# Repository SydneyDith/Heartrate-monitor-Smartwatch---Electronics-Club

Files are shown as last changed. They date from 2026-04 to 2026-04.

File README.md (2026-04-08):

# Heart rate Monitor Smartwatch - Electronics Club
Led the development of a heart rate monitor smartwatch based on the ATmega328P microcontroller with a group of 4. Utilized several sensors to send/receive data via I2C communication protocol using C based Arduino IDE. Designed custom PCB while analyzing several datasheets to reduce device size and create a more ergonomic user experience. 

This project was separated into two teams. Team 1 specialized in hardware development and was responsible for component selection, power distribution, datasheet analysis and PCB design. Team 2 interfaced with the microcontroller and sensors in the Arduino IDE by utilizing libraries like PulseSensor Playground, U8g2, and RTClib. While I primarily led Team 1, I also served as the mediator for cross-team communication to ensure hardware and software supported each other.

## Smartwatch Project Objectives

| Feature | Description | Goal |
| :--- | :--- | :--- |
| **Heart Rate Monitor** | Integrate Pulse Sensor | Provides heart rate measurements. |
| **OLED Display** | 1.3" SH1106 OLED Display | Clear visual output for biometric data and time. |
| **Timekeeping** | RTC (Real-Time Clock) | Maintain precise time and date. |
| **Power System** | Rechargeable LiPo | Provides rechargeable power. |

Throughout every iteration of this project we may have moved forward with different components that better fit our needs, however, the 4 underlying features above were included in every version of this project. 

## Proof of Concept: ***May 2025***

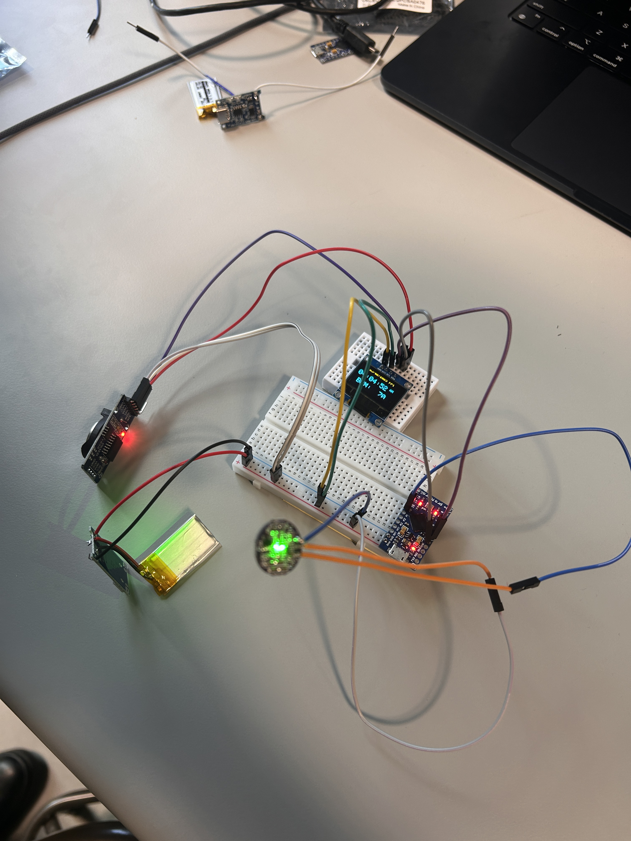
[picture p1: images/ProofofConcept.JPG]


The image above shows the first prototype of our Smartwatch. This version was based off of Arduino's smallest dev board the Pro Mini which houses the ATmega328P as its microcontroller (we would later use on the final versions of our project). To provide the functionalities we desired, we ordered several Arduino compatible modules that we could power and hook up to specific digital pins on the Pro Mini. In the table below is the comprehensive parts list we used for our first prototype:

| Feature | Part Name | Image |
| :--- | :--- | :--- |
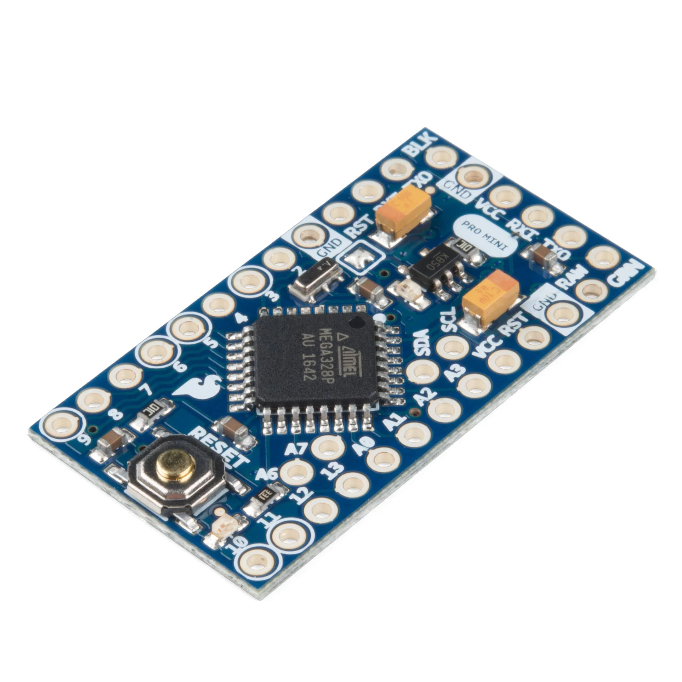
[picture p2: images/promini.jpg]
| **Microcontroller** | Arduino Pro Mini |  |
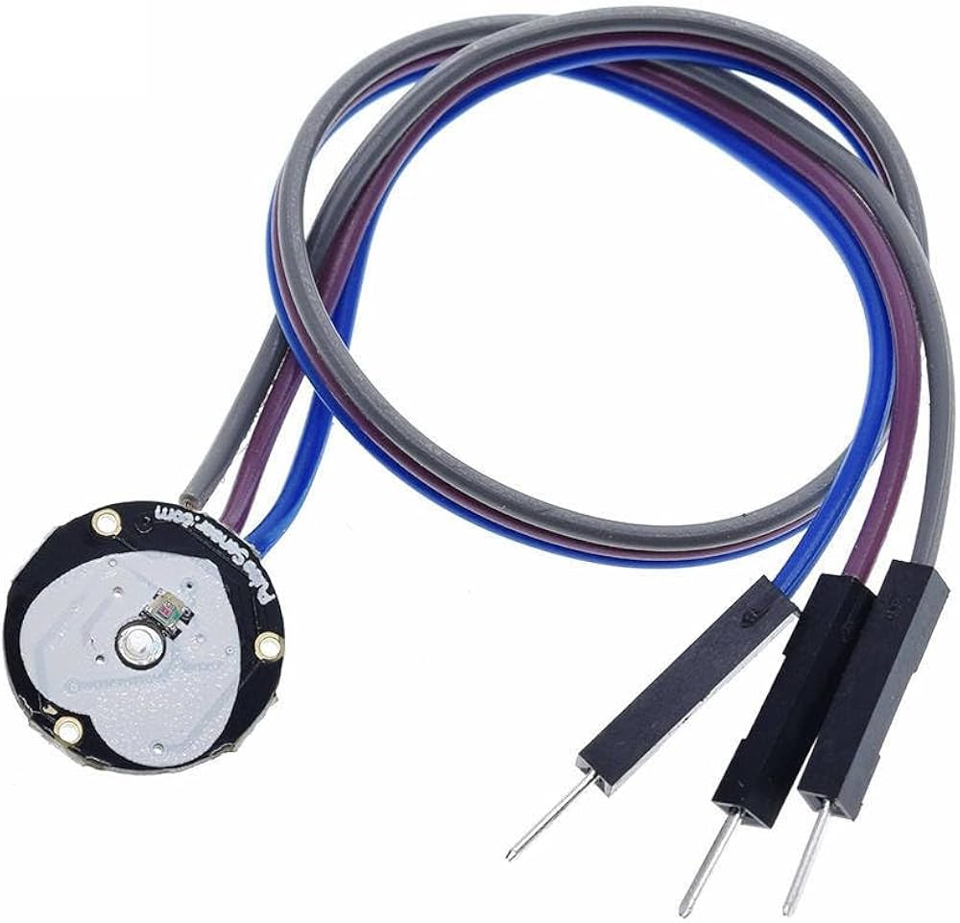
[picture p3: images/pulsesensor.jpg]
| **Heart Rate Monitor** | Integrate Pulse Sensor | |
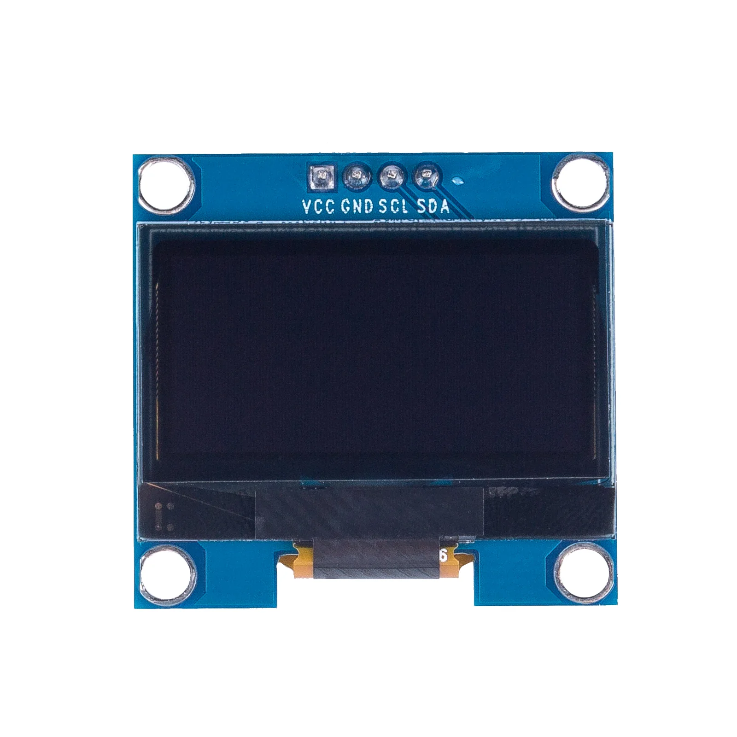
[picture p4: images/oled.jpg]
| **OLED Display** | OLED Display |  |
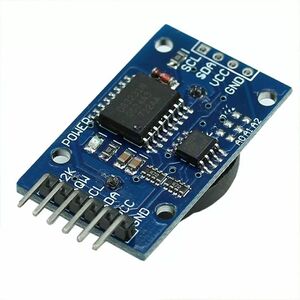
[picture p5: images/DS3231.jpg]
| **Timekeeping** | RTC (Real-Time Clock) | |
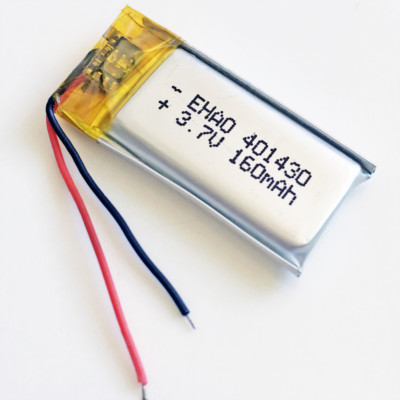
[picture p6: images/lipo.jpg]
| **Power System** | Rechargeable LiPo | |

### Pulse Sensors Issues
The OLED display shows time, date, and current heart rate reading. Team 2 was able to program the Pro Mini to read from the RTC module and pulse sensor then display the results on the OLED. The pulse sensor results fluctuated quite a bit. After some research, we attributed this to the quality of the sensor itself. Many cheap pulse sensors use a method called photoplethysmography (PPG) to measure the change in blood volume in your capillaries as your heart beats. The pulse sensor module uses a green LED to shine light into the capillaries and measures the amount of light reflected back using a photodetector. Ideally, the pulse sensor can translate this information into an accurate heart rate reading. PPG is cheap, however, it's very sensitive to real world motion, ambient light interference and sensor contact. 
[*references*](https://www.sciencedirect.com/topics/engineering/sensor-pulse#:~:text=A%20pulse%20sensor%20is%20defined,Arduino%20for%20health%20monitoring%20applications.)

More accurate pulse sensors (professional grade) cost hundreds or thousands of dollars. Luckily, there is a cheaper PPG option, the MAX30102, that uses multi-wavelength LEDs and has an on-board processing IC. It also includes SpO2 readings as an added feature. We later decided to switch to the MAX30102 pulse oximeter to replace the pulse sensor module.

### First Prototype: ***May 2025***
To turn our breadboard prototype into something that resembled a watch, we soldered the modules together trying to keep wires as short as possible. The following video shows the result:

| Top View | Side View 1 | Side View 2 | Video |
| :---: | :---: | :---: | :---: |
|  |  |  | <video src="https://github.com/user-attachments/assets/febb02ad-0546-478b-9966-6aa6d14cd212" width="120" controls></video> |

During this stage of the design process, my team and I realized that size was going to be our main constraint. The form factor shown above is ridiculously large to be comfortably worn on the wrist. After the 3D printed housing, my team and I estimated our first prototype's dimensions would be around 45mm x 45mm x 50mm, which would better be used as a desk clock. After doing more research and conversing amongst ourselves and with our peers, we decided to create a custom PCB that would eliminate many of the unnecessary functions our sensor modules included. For example, the Pro Mini included headers for every I/O pin, only ~5 of which were essential and the DS3231 RTC module included alarm and 32kHz square wave output functionalities that were out of the scope of this project. By creating a custom PCB, we could limit unnecessary functions of our modules, reducing size and creating a more ergonomic design.

## Schematic Design: ***February 2026***

Although we decided to transition to the MAX30102 pulse oximeter, our proof of concept was still valid as we are only replacing the pulse sensor and there are countless resources online showing the MAX30102's compatibility with the 328P. With this, we decided to move forward into PCB design for our second prototype.

To minimize the size of our PCB, we only wanted to include functionalities that were (for the most part) strictly necessary for our smartwatch. We would essentially be stripping the modules from our prototype and putting everything on one PCB. First, we researched the bare minimum requirements for the ATmega328P microcontroller. Using the microcontroller's datasheet and online resources, we were able to simplify the circuit down to a few capacitors and a pull-up resistor. There was an optional 16MHz external crystal oscillator that was typically used with the 328P, however, these clock speeds wouldn't be necessary for our use case. We could instead use the 8 MHz internal oscillator. We used similar techniques to reduce the size of our RTC and sensor modules.

The final schematic for Prototype 2 is shown below: (*see below the image for in-depth detail about the schematic*)

<p align="center">
  
</p>

<p align="center">
  <a href="./images/schem.pdf">📄 View Full Schematic (PDF)</a>
</p>

To use the 328P's 8 MHz internal clock, we were required to run the microcontroller at 3.3V, however, our LiPo was 4.2V-3.7V. To fix this, we simply included a 3.3V Low Dropout regulator (LDO) (U2) after the power switch. This reduced our input voltage to a clean 3.3V. Additionally, the MAX30102 operates at 1.8V, so we included a second LDO (U5) that reduced the 3.3V line to 1.8V which could be used for the pulse oximeter's input voltage. However, every other IC was powered by the 3.3V line. The I2C communication lines from the RTC and pulse oximeter required two 4.7k pull-up resistors to the 3.3V line as per the datasheets. We also included several input capacitors and decoupling capacitors on the RTC and pulse oximeter as the datasheet heavily recommended or required them. 

We also included 4 pin headers: I2C clock, I2C data, +3.3V, and GND for the SH1106 OLED display. We plan to solder the 4 required pins directly to the OLED module used in the previous prototype. 

Since there is no longer a Micro USB port on our microcontroller (like the Pro Mini), we must use a [USB to Serial Converter](https://www.amazon.com/NOYITO-CP2102-Converter-Downloader-Arduino/dp/B07D54K82D) so we can connect and upload code to the 328P using UART communication. 

Upon doing further research on the microcontroller, we encountered a problem. Factory new ATmega328P chips often do not come with a pre-installed bootloader. The bootloader is an essential piece of software that allows the microcontroller to communicate via UART. Without UART communication, we would not be able to upload our code using the USB to serial converter. We researched methods to solve this issue. We found a process called In-System Programming (ISP) that requires an Arduino to flash the bootloader onto a blank ATmega328P. To do this we simply created 4 more pin headers that connected to specific pins on the 328P. These were: MOSI, MISO, SCK, and RESET. Using these four SPI pins alongside +3.3V, and GND, we could successfully bootload the chip using an external Arduino Nano allowing us to program through UART communication.
[Bootloader Procedure (PDF)](images/Smartwatch%20Bootloader%20Procedure.pdf).

## PCB Design: ***April 2026***

Final PCB design: (46mm x 39mm x 5mm)

<p align="center">
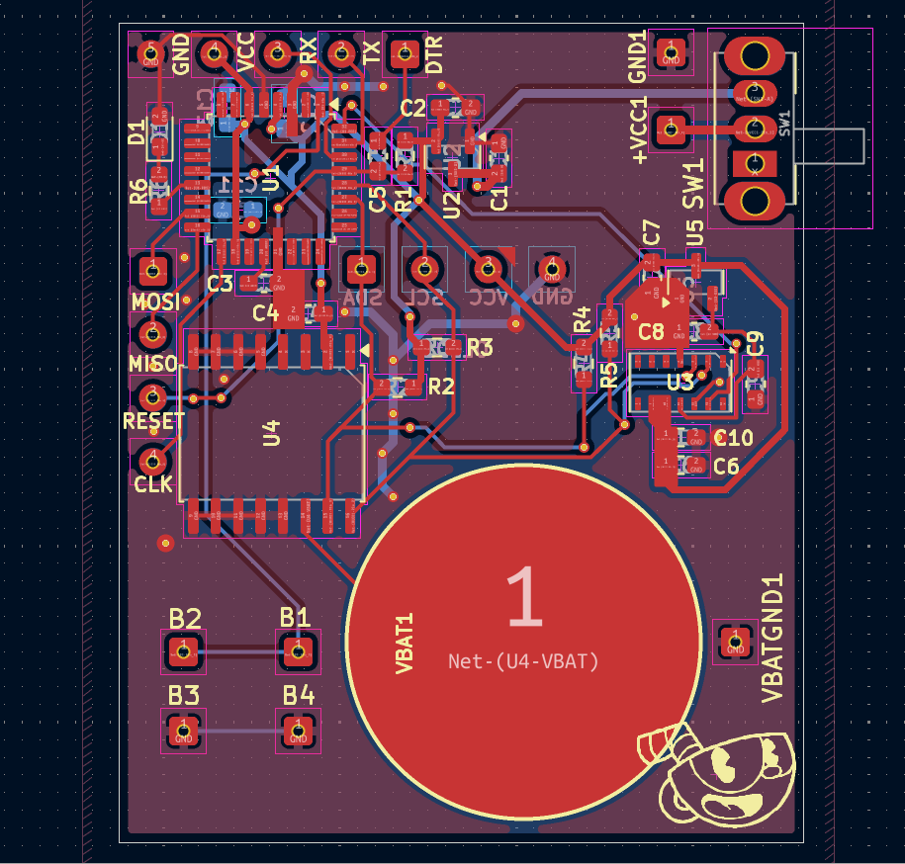
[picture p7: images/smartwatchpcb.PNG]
  
</p>

| Front PCB view (*OLED will be connected to the 4 pinheaders*) | Back PCB view |
| :---: | :---: |
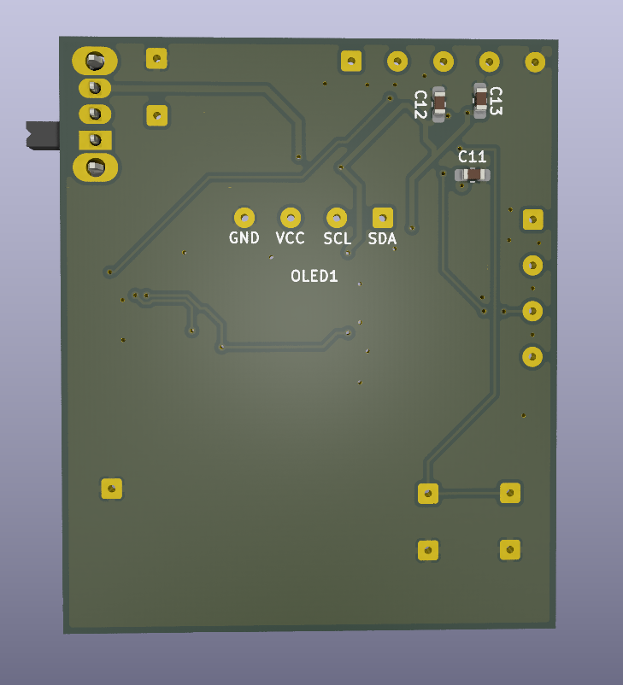
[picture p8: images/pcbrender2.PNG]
PCB Render 2
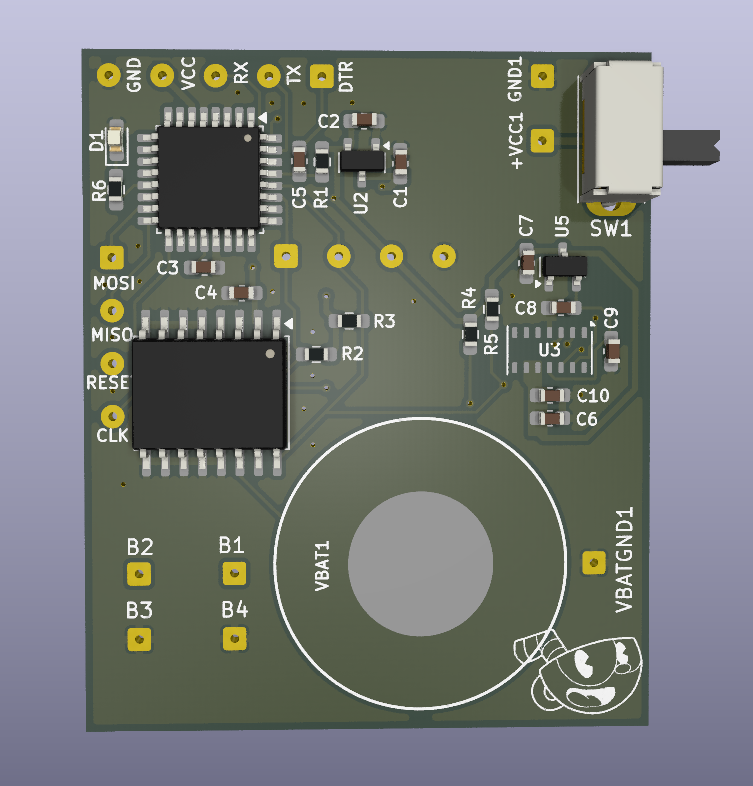
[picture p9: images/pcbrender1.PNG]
PCB Render 1
|  |  |

The images and 3D renders above show the final PCB design for Prototype 2. Now I plan to move on to the assembly phase when the PCB and components arrive in the coming weeks.
## TO DO

- [ ] **Bootload the ATmega328P**
    - Follow the [bootloader procedure](images/Smartwatch%20Bootloader%20Procedure.pdf)
    - Ensure the microcontroller communicates via UART
    - Test Blink sketch with on-board LED
- [ ] **Initial Soldering & Assembly**
    - Solder MAX30102 and coin cell battery using a heat gun
    - Assemble the remainder of the PCB
    - Verify MAX30102 has a clear line of sight to the user's skin
- [ ] **Sensor Testing**
    - [ ] Pulse Oximeter: Verify accurate heart rate/SpO2 readings
    - [ ] OLED: Ensure proper display rendering
    - [ ] RTC: Confirm accurate timekeeping
- [ ] **Power System Setup**
    - Integrate LiPo battery and external charging circuit
- [ ] **Performance Testing**
    - [ ] Heart rate accuracy
    - [ ] Battery life duration
    - [ ] Charge time verification
- [ ] **Housing**
    - Design 3D printed enclosure
- [ ] **Interpret Tests**
    - Document changes for Prototype 3

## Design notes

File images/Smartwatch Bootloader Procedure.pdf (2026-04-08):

### Phase 1: Minimal Assembly

Focus only on getting the brain to wake up. Solder the ATmega328P-AU first, then add the 10kΩ pull-up resistor between Reset and 3.3V and the 0.1μF decoupling caps near the power pins. Before applying power, use a magnifying glass to check for solder bridges, especially on the 0.8mm pitch SPI pins (15, 16, 17, and 29).

### Phase 2: Flashing the Bootloader

Since new chips are blank, you will use an Arduino Nano as an ISP (In-System Programmer).

1. Nano Setup: Upload the ArduinoISP sketch to the Nano. Once done, stick a 10μF capacitor between the Nano’s Reset and GND to prevent it from resetting during the process.
2. Wiring: Connect the Nano to your PCB using the following map:
- MOSI/MISO/SCK: Pins 11, 12, 13 to pins 15, 16, 17.
- Reset: Nano D10 to PCB pin 29.
- Power: Standard 3.3V and GND.
3. The Burn: In the IDE, select Arduino Pro or Pro Mini (3.3V, 8 MHz), change the programmer to Arduino as ISP, and select Burn Bootloader.

### Phase 3: UART and Blink Test

With the bootloader installed, your chip should now talk over UART. Switch to your USB-to-Serial adapter and connect to your 5-pin header. Try uploading a basic Blink sketch. If the LED on your board starts flashing, your microcontroller and UART circuit are officially working.

### Phase 4: Full Assembly and I2C Check

Now you can populate the rest of the board: the LDO regulator, the MAX30102 sensor, and the OLED. To verify the hardware, run an I2C Scanner sketch. If the serial monitor shows addresses 0x57 and 0x3C, your sensors are correctly addressed and the bus is solid.

### Extra Info

- Use internal pullup on int pin PD3 so it isn’t floating and 328p knows when its low or high.
- When bootloading the new chip, use a 10uF cap on the nano from RESET to GND. This prevents the nano from resetting itself and allows it to run the ISP bootloader.
- Hook up the nano to MOSI, MISO, RESET, and CLK pin headers, then VCC and GND to the available headers at the OLED or the serial communication bus.

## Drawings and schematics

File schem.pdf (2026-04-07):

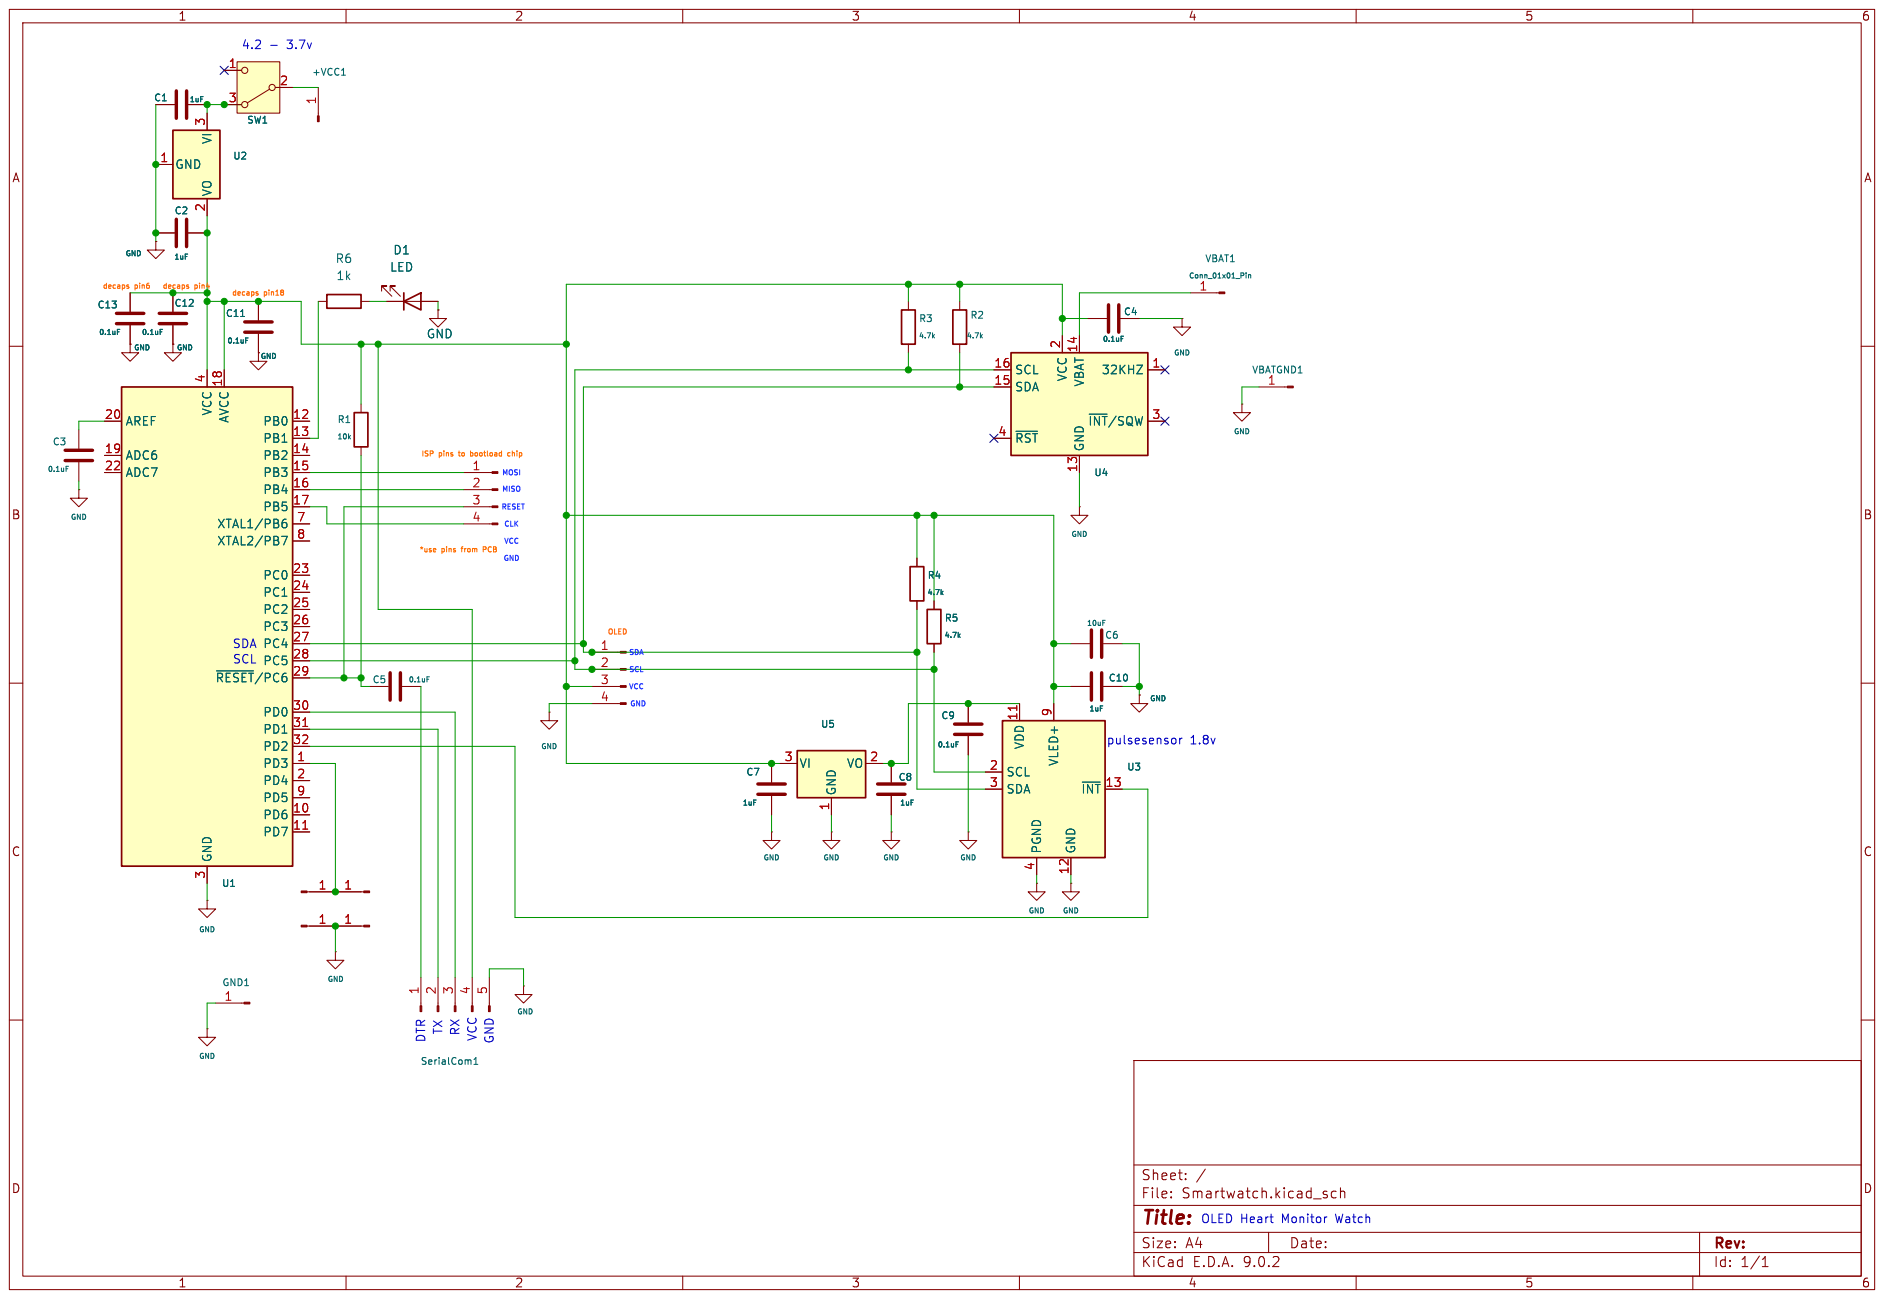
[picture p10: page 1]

ISP pins to bootload chip MOSI SDA

*use pins from PCB SCL

Id: 1/1 Title: File: Smartwatch.kicad_sch Sheet: /

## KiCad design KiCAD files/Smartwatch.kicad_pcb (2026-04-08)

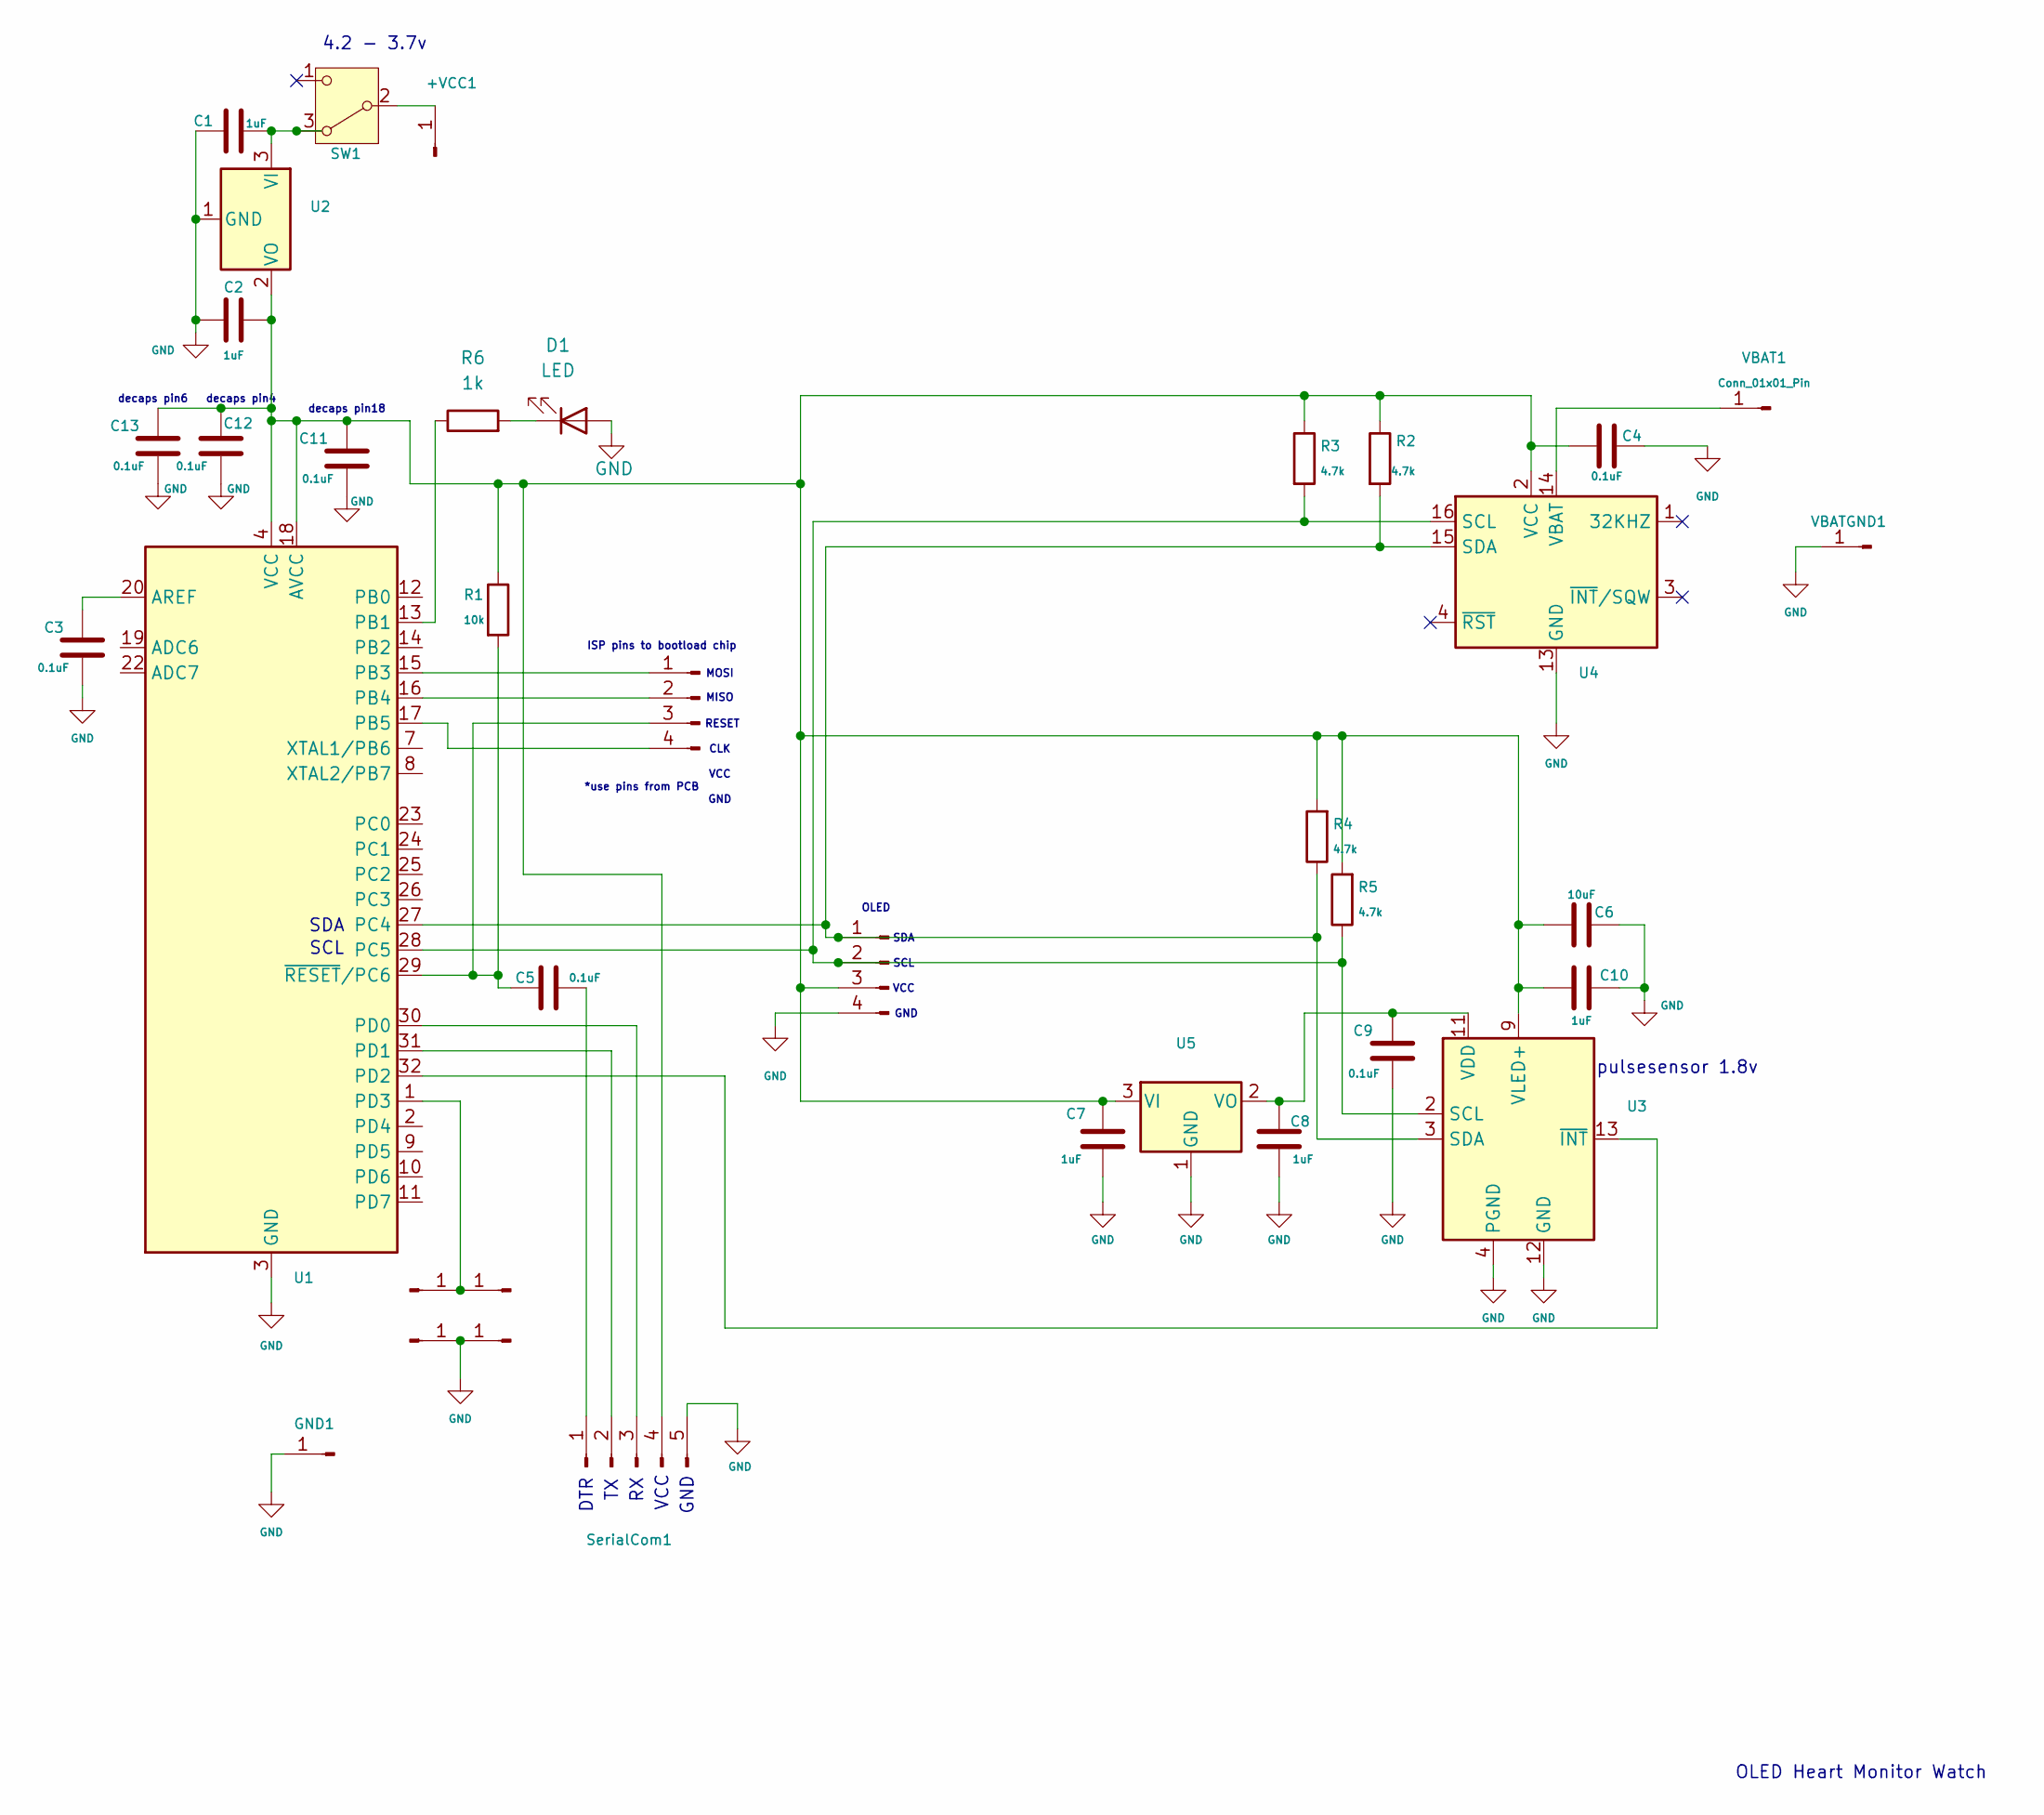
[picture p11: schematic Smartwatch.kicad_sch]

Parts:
+VCC1: Conn_01x01_Pin; SolderWire-0.1sqmm_1x01_D0.4mm_OD1mm
Button1, Button2, Button3, Button4: Conn_01x01_Pin; SolderWire-0.1sqmm_1x01_D0.4mm_OD1mm
C1, C2, C7, C8, C10: 1uF; C_0603_1608Metric_Pad1.08x0.95mm_HandSolder
C3, C4, C5, C9, C11, C12, C13: 0.1uF; C_0603_1608Metric_Pad1.08x0.95mm_HandSolder
C6: 10uF; C_0603_1608Metric_Pad1.08x0.95mm_HandSolder
D1: LED; LED_0603_1608Metric_Pad1.05x0.95mm_HandSolder
GND1: Conn_01x01_Pin; SolderWire-0.1sqmm_1x01_D0.4mm_OD1mm
OLED1, OLED2: Conn_01x04_Pin; SolderWire-0.1sqmm_1x04_P3.6mm_D0.4mm_OD1mm
R1: 10k; R_0603_1608Metric_Pad0.98x0.95mm_HandSolder
R2, R3, R4, R5: 4.7k; R_0603_1608Metric_Pad0.98x0.95mm_HandSolder
R6: 1k; R_0603_1608Metric_Pad0.98x0.95mm_HandSolder
SW1: SW_Nidec_CAS-120A1; SW_Slide_SPDT_Angled_CK_OS102011MA1Q
SerialCom1: Conn_01x05_Pin; SolderWire-0.1sqmm_1x05_P3.6mm_D0.4mm_OD1mm
U1: ATmega328P-A; TQFP-32_7x7mm_P0.8mm
U2: MCP1700x-330xxTT; SOT-23
U3: MAX30102; Maxim_OLGA-14_3.3x5.6mm_P0.8mm
U4: DS3231M; SOIC-16W_7.5x10.3mm_P1.27mm
U5: MCP1700x-180xxTT; SOT-23
VBAT1: Conn_01x01_Pin; SolderWire-0.1sqmm_1x01_D0.4mm_OD1mm
VBATGND1: Conn_01x01_Pin; SolderWire-0.1sqmm_1x01_D0.4mm_OD1mm

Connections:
GND: Button3.1, Button4.1, C1.1, C2.2, C3.2, C4.2, C6.2, C7.1, C8.1, C9.1, C10.2, C11.2, C12.2, C13.2, D1.2 (A), GND1.1, OLED1.4, SerialCom1.5, U1.3 (GND), U1.5 (GND), U1.21 (GND), U2.1 (GND), U3.4 (PGND), U3.12 (GND), U4.5 (GND), U4.6 (GND), U4.7 (GND), U4.8 (GND), U4.9 (GND), U4.10 (GND), U4.11 (GND), U4.12 (GND), U4.13 (GND), U5.1 (GND), VBATGND1.1
unnamed: +VCC1.1, SW1.2 (B)
unnamed: Button1.1, Button2.1, U1.1 (PD3)
unnamed: D1.1 (K), R6.2
unnamed: OLED1.1, R2.2, R4.1, U1.27 (PC4), U3.3 (SDA), U4.15 (SDA)
unnamed: OLED1.2, R3.2, R5.1, U1.28 (PC5), U3.2 (SCL), U4.16 (SCL)
unnamed: C2.1, C4.1, C6.1, C7.2, C10.1, C11.1, C12.1, C13.1, OLED1.3, R1.1, R2.1, R3.1, R4.2, R5.2, SerialCom1.4, U1.4 (VCC), U1.6 (VCC), U1.18 (AVCC), U2.2 (VO), U3.9 (VLED+), U3.10 (VLED+), U4.2 (VCC), U5.3 (VI)
unnamed: OLED2.1, U1.15 (PB3)
unnamed: OLED2.2, U1.16 (PB4)
unnamed: C5.2, OLED2.3, R1.2, U1.29 (~RESET/PC6)
unnamed: OLED2.4, U1.17 (PB5)
unnamed: C1.2, SW1.3 (A), U2.3 (VI)
unnamed: C5.1, SerialCom1.1
unnamed: SerialCom1.2, U1.31 (PD1)
unnamed: SerialCom1.3, U1.30 (PD0)
unnamed: C3.1, U1.20 (AREF)
unnamed: R6.1, U1.13 (PB1)
unnamed: U1.32 (PD2), U3.13 (~INT)
unnamed: C8.2, C9.2, U3.11 (VDD), U5.2 (VO)
unnamed: U4.14 (VBAT), VBAT1.1

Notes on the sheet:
4.2 - 3.7v
MOSI
CLK
MISO
VCC
VCC
SCL
SDA
GND
*use pins from PCB
OLED Heart Monitor Watch
pulsesensor 1.8v
decaps pin4
decaps pin18
decaps pin6
ISP pins to bootload chip
DTR
OLED
RESET

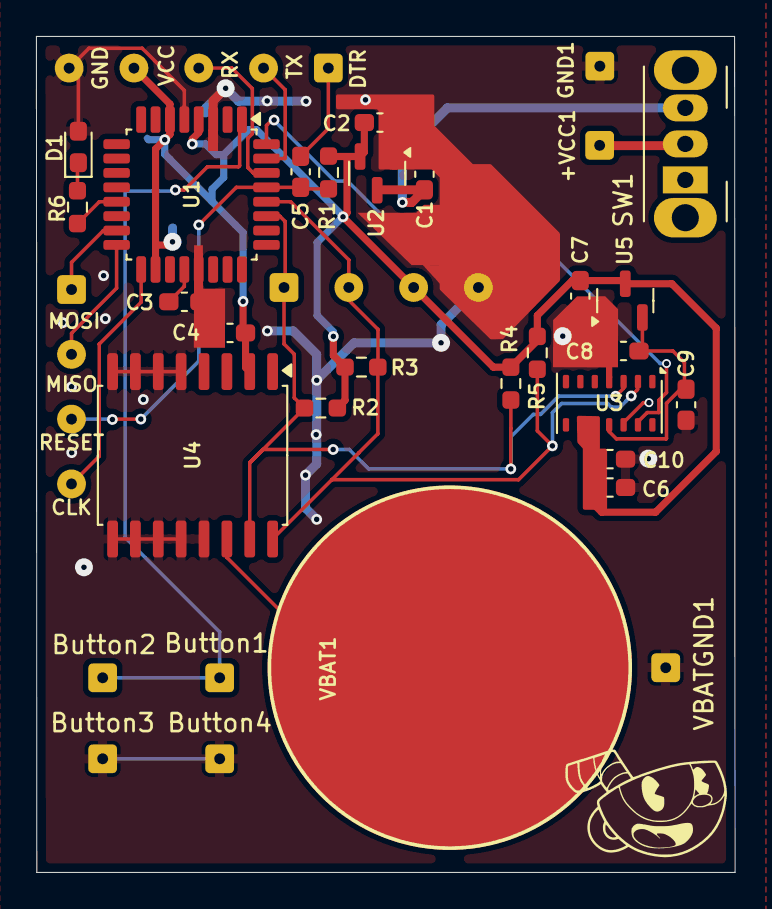
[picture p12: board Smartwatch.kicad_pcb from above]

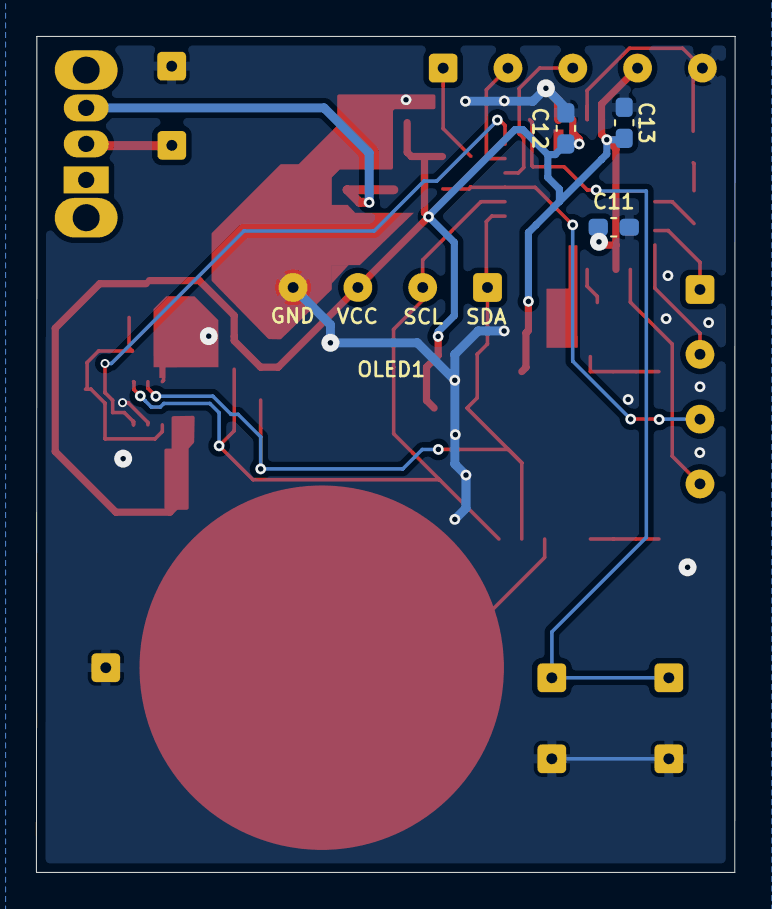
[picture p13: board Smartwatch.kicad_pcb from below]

Board: 2 copper layers, 38.8 x 46.4 mm, 37 parts (4 on the bottom side), 20 nets.
